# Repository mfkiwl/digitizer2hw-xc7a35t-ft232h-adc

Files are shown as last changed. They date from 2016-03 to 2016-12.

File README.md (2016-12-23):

# Digitizer2 TDC hardware
The digitizer2 project is a low-cost, high speed analog-to-digital converter with customizable signal processing logic.

Hardware
---
- Xilinx Artix7 FPGA (XC7A35T)
- 500 MHz, 12bit ADC (ADS5403)
- DDR3 Memory, 128 MB (MT41J128M16)
- USB 2.0, Hi-Speed (FT2232H)

Related repositories
---
- [FPGA device server](https://github.com/pwuertz/fpga-device-server)
- [Digitizer2 Firmware](https://github.com/pwuertz/digitizer2fw)
- [Digitizer2 Hardware](https://github.com/pwuertz/digitizer2hw)

License
---
This project is free software. You can redistribute it and/or modify it under the terms of the [GNU General Public License](COPYING.txt).

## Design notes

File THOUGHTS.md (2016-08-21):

PCB Buildup
===========

6 Layer Option
--------------

Eurocircuits 6 layer, 35µm copper inner/outer:
- layer 1
- prepreg, 0.2mm
- layer 2
- core, 0.36mm
- layer 3
- prepreg, 0.3mm
- layer 4
- core, 0.36mm
- layer 5
- prepreg, 0.2mm
- layer 6

LVDS 100 Ohm, 2x signals outer:
- reference layers 2, 3, 5
- signal layers 1, 6 (outer): W = 0.19mm, S = 0.15mm, D >= 0.3mm
- signal layer 4 (inner): W = 0.15mm, S = 0.165mm, D >= 0.34mm

LVDS 100 Ohm, 2x signals inner:
- reference layers 1, 3, 4, 6
- signal layers 2, 5 (inner): W = 0.13mm, S = 0.19mm, D >= 0.4mm

USB 90 Ohm:
- signal layers 2, 5 (inner): W = 0.163mm, S = 0.19mm

FPGA Solution
=============

FPGA:
XC7A35T-2FTG256I
Artix7, 35T, FTG256, Speed Grade 2
http://www.digikey.de/product-detail/en/xilinx-inc/XC7A35T-2FTG256I/122-1912-ND/5039076

Memory:
MT41J128M16JT-125
IC DDR3 SDRAM 2GBIT 96FBGA
RZQ/4: 60 Ohm (easier for routing?)
RZQ/6: 40 Ohm

ADC Solution
============

500 Msps, 12 bit, 1 Channel

AD9434BCPZ-500
- Analog Devices, QFP Package
- 155€, DigiKey

ADS5403
- Texas Instruments, BGA Package
- 142€, DigiKey
- Pin compatible with 2 channel version
- LVDS capable clock input

FPGA Banks
==========

The I/O in 7 series FPGAs are classed as high range (HR) or high performance (HP). The HR I/Os offer the widest range of voltage support, from 1.2V to 3.3V. The HP I/Os are optimized for highest performance operation, from 1.2V to 1.8V.
- Artix only provides HR banks

The configuration banks voltage select pin (CFGBVS) must be set to a High (VCCO_0) or Low (GND) to set the configuration and JTAG I/O in banks 0, 14, and 15 for 3.3V/2.5V or 1.8V/1.5V operation, respectively.
- use 3.3V for bank 0 (JTAG-FTDI), set CFGBVS to VCCO_0
- use JTAG only configuration mode so bank 14 and 15 are not restricted to 3.3V (http://www.xilinx.com/support/answers/57045.html)

Configuration
=============

JTAG only configuration mode: M[2:0] <= "101"

Capacitor Selection
===================

Check DC Bias: http://ds.murata.co.jp/software/simsurfing

10nF, 0402, GRM155R71C103KA01
0.1uF, 0402, GRM155R71A104KA01
0.47uF, 0402, GRM155R60J474KE19 (up to 2.5V)
1uF, 0402, GRM155R61A105KE15D (up to 2.5V)
4.7uF, 0805, GRM21BR71A475KA73 (up to 3.3V)
47uF, 1210, GRM32ER70J476ME20L (up to 2.5V)
10uF, 1206, GRM32DR61C106KA01 (up to 5.0V)

Power Supply
============

FPGA Core
- 1.0V (http://www.digikey.de/product-detail/de/analog-devices-inc/ADP2108AUJZ-1.0-R7/ADP2108AUJZ-1.0-R7CT-ND/2355507)
FPGA LVDS Banks
- 2.5V LM3671MF-2.5

ADC Supply
- 2.5V TPS79625DCQ
2mA
- 1.8V TPS79618DCQ
65mA + 35mA + 170mA + 90mA = 360mA
- 3.3V TPS79633DCQ
170mA

Modular Design
==============
Board-To-Board Differential Connectors
http://www.digikey.de/product-detail/de/samtec-inc/QTH-040-01-L-D-DP-A/SAM8849-ND/2345118
http://www.digikey.de/product-detail/de/samtec-inc/QSH-040-01-L-D-DP-A/SAM8843-ND/2345116

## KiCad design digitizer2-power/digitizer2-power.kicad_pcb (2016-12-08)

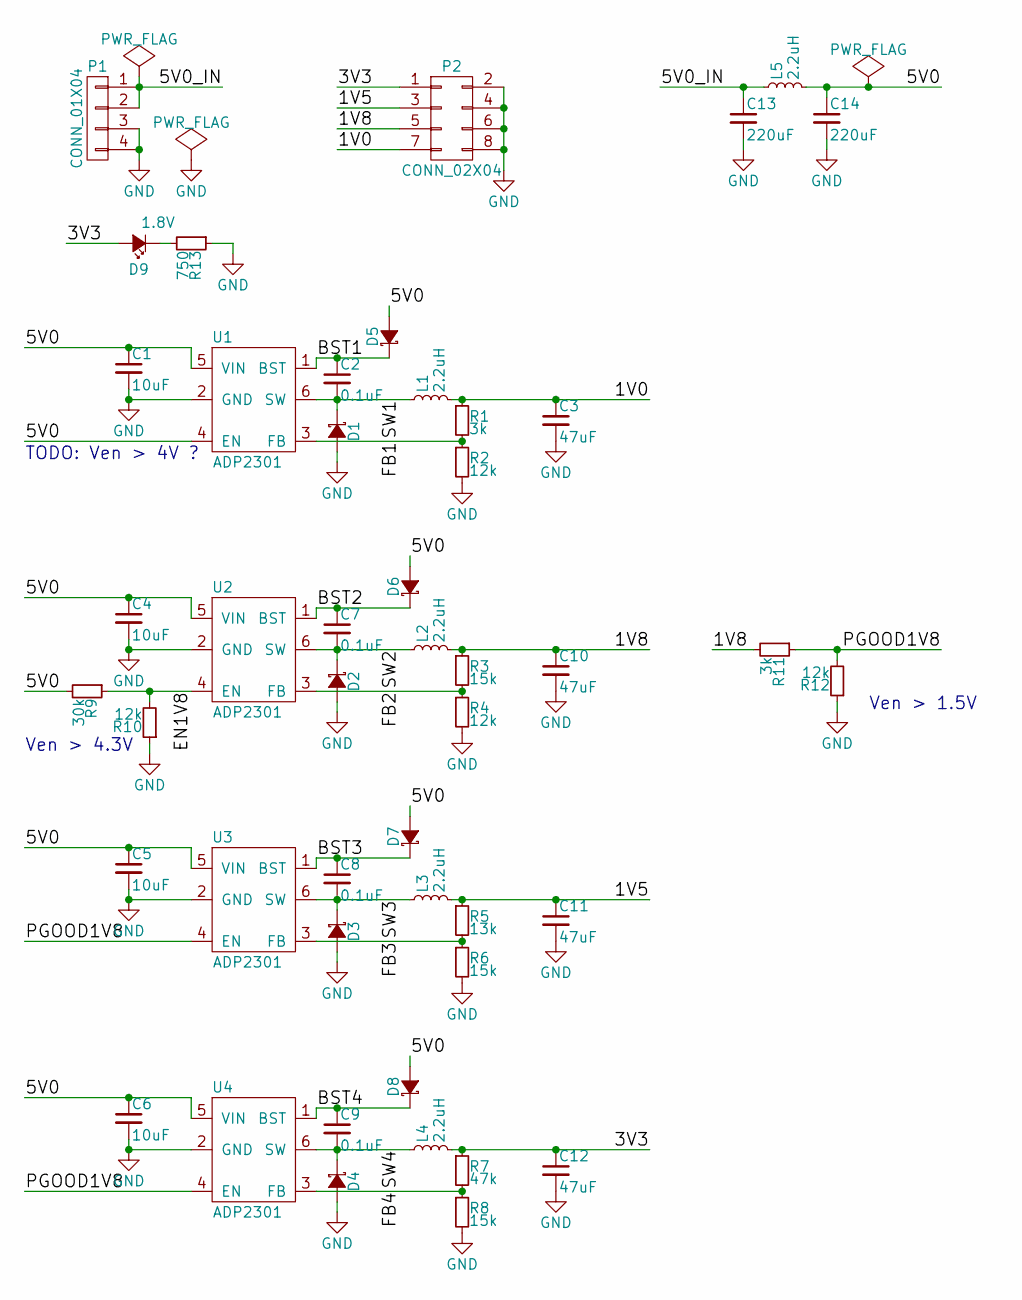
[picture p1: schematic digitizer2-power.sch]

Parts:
C1, C4, C5, C6: 10uF; C_1206; MPN GRM32DR61C106KA01L
C2, C7, C8, C9: 0.1uF; C_0603_HandSoldering; MPN GRM188R72A104KA35D
C3, C10, C11, C12: 47uF; C_1210; MPN GRM32ER61A476KE20L
C13, C14: 220uF; c_elec_5x5.7; MPN 6SVPE220MW
D1, D2, D3, D4: D_Schottky_Small; SMA_Standard; MPN B230A-13-F
D5, D6, D7, D8: D_Schottky_Small; SOD-123; MPN BAT42W
D9: 1.8V; LED_0603
L1, L2, L3, L4, L5: 2.2uH; IHLP-1212BZ-11; MPN IHLP1212BZER2R2M11
P1: CONN_01X04; Pin_Header_Straight_1x04
P2: CONN_02X04; Pin_Header_Straight_2x04
R1, R11: 3k; R_0603_HandSoldering
R2, R4, R10, R12: 12k; R_0603_HandSoldering
R3, R6, R8: 15k; R_0603_HandSoldering
R5: 13k; R_0603_HandSoldering
R7: 47k; R_0603_HandSoldering
R9: 30k; R_0603_HandSoldering
R13: 750; R_0603_HandSoldering
U1, U2, U3, U4: ADP2301; SOT-23-6; MPN ADP2301AUJZ-R7

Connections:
/1V0: C3.1, L1.2, P2.7, R1.1
/1V5: C11.1, L3.2, P2.3, R5.1
/1V8: C10.1, L2.2, P2.5, R3.1, R11.2
/3V3: C12.1, D9.2 (A), L4.2, P2.1, R7.1
/5V0: C1.1, C4.1, C5.1, C6.1, C14.1, D5.2 (A), D6.2 (A), D7.2 (A), D8.2 (A), L5.2, R9.2, U1.4 (EN), U1.5 (VIN), U2.5 (VIN), U3.5 (VIN), U4.5 (VIN)
/5V0_IN: C13.1, L5.1, P1.1, P1.2
/BST1: C2.1, D5.1 (K), U1.1 (BST)
/BST2: C7.1, D6.1 (K), U2.1 (BST)
/BST3: C8.1, D7.1 (K), U3.1 (BST)
/BST4: C9.1, D8.1 (K), U4.1 (BST)
/EN1V8: R9.1, R10.2, U2.4 (EN)
/FB1: R1.2, R2.1, U1.3 (FB)
/FB2: R3.2, R4.1, U2.3 (FB)
/FB3: R5.2, R6.1, U3.3 (FB)
/FB4: R7.2, R8.1, U4.3 (FB)
/PGOOD1V8: R11.1, R12.2, U3.4 (EN), U4.4 (EN)
/SW1: C2.2, D1.1 (K), L1.1, U1.6 (SW)
/SW2: C7.2, D2.1 (K), L2.1, U2.6 (SW)
/SW3: C8.2, D3.1 (K), L3.1, U3.6 (SW)
/SW4: C9.2, D4.1 (K), L4.1, U4.6 (SW)
GND: C1.2, C3.2, C4.2, C5.2, C6.2, C10.2, C11.2, C12.2, C13.2, C14.2, D1.2 (A), D2.2 (A), D3.2 (A), D4.2 (A), P1.3, P1.4, P2.2, P2.4, P2.6, P2.8, R2.2, R4.2, R6.2, R8.2, R10.1, R12.1, R13.1, U1.2 (GND), U2.2 (GND), U3.2 (GND), U4.2 (GND)
unnamed: D9.1 (K), R13.2

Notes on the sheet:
TODO: Ven > 4V ?
Ven > 4.3V
Ven > 1.5V

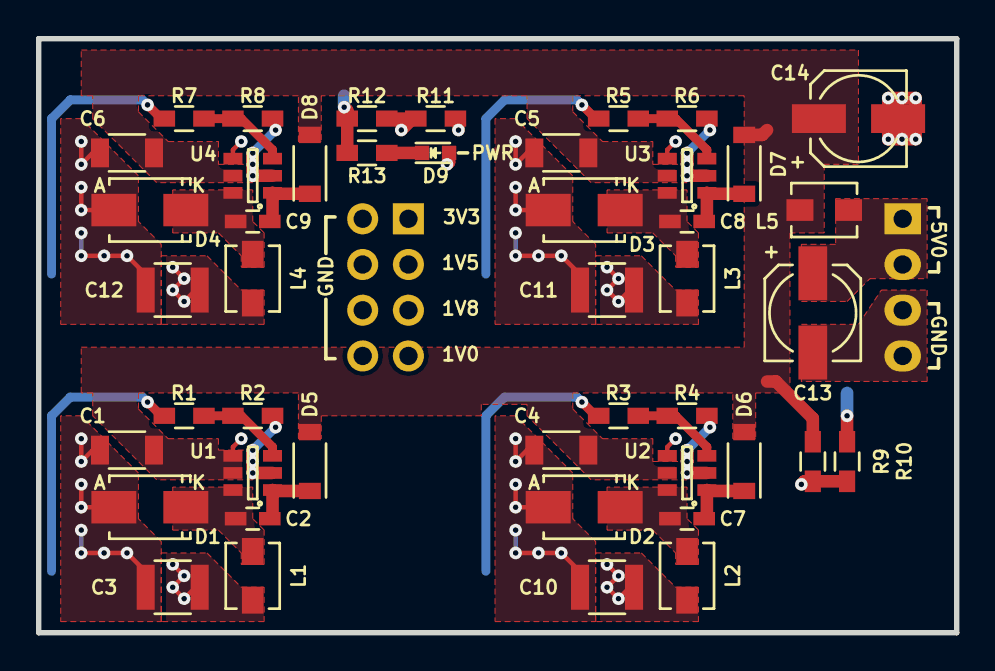
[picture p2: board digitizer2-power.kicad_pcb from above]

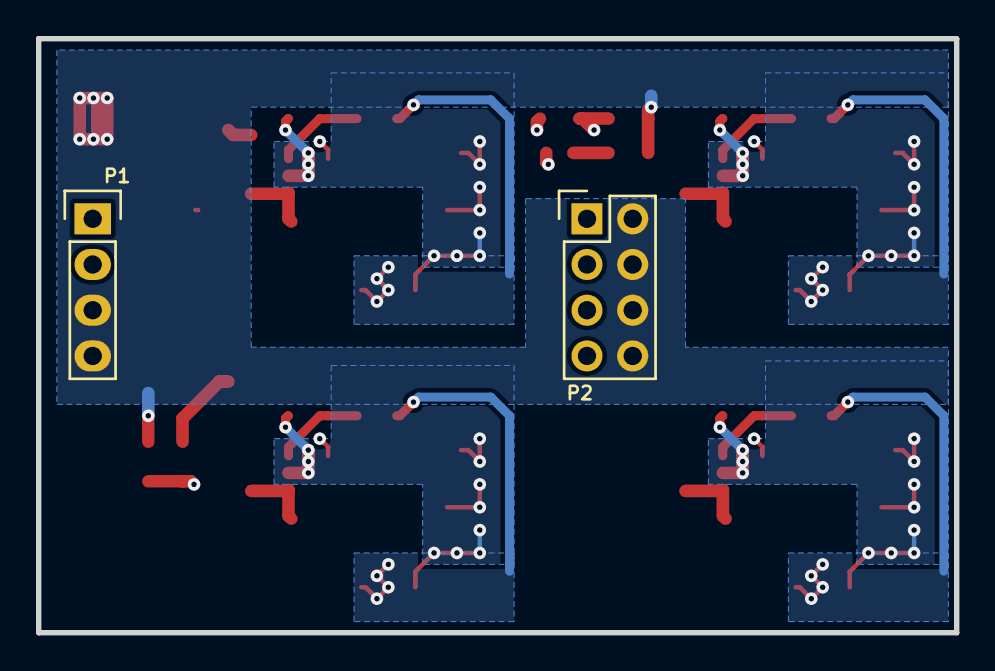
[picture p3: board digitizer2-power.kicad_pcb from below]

Board: 4 copper layers, 51.0 x 33.0 mm, 47 parts (2 on the bottom side), 22 nets.

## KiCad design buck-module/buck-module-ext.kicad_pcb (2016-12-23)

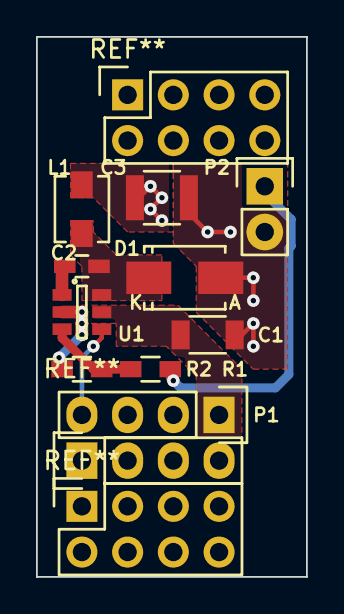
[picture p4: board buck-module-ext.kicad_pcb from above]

Board: 2 copper layers, 15.0 x 30.0 mm, 10 parts (0 on the bottom side), 7 nets.

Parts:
C1: 10uF; C_1206
C2: 0.1uF; C_0603_HandSoldering
C3: C_Small; C_1210
D1: D_Schottky_Small; SMA_Standard
L1: 2.2uH; IHLP-1212BZ-11
P1: CONN_01X04; Pin_Header_Straight_1x04
P2: CONN_01X02; Pin_Header_Straight_1x02
R1: div1; R_0603_HandSoldering
R2: div2; R_0603_HandSoldering
U1: ADP2301; SOT-23-6

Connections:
/BST: C2.1, U1.1
/EN: P1.4, U1.4
/FB: R1.2, R2.1, U1.3
/SW: C2.2, D1.1, L1.1, U1.6
/VIN: C1.1, P1.1, U1.5
/VOUT: C3.1, L1.2, P2.1, R1.1
GND: C1.2, C3.2, D1.2, P1.2, P1.3, P2.2, R2.2, U1.2

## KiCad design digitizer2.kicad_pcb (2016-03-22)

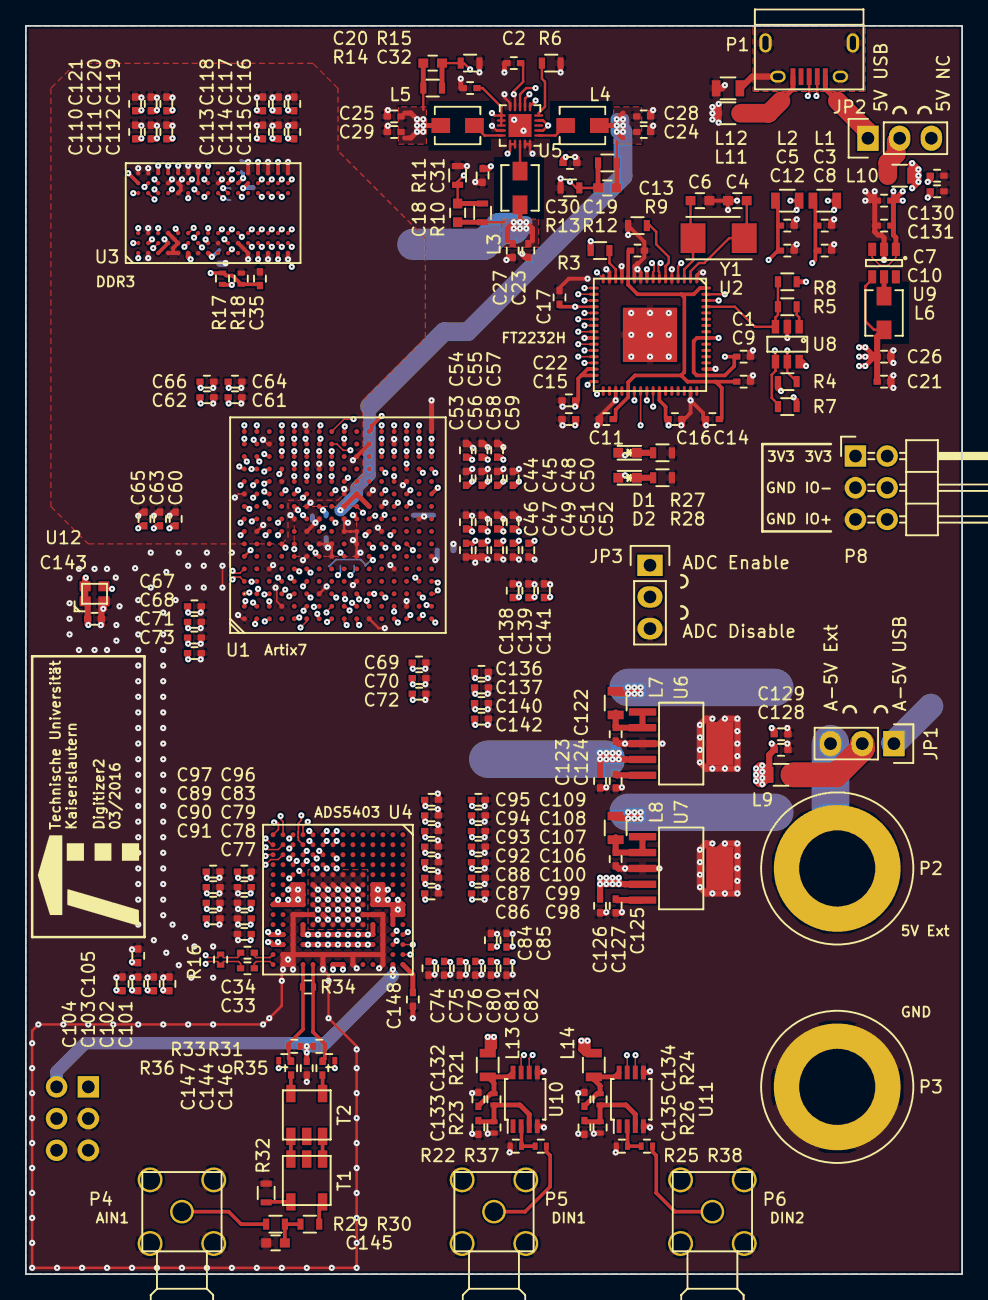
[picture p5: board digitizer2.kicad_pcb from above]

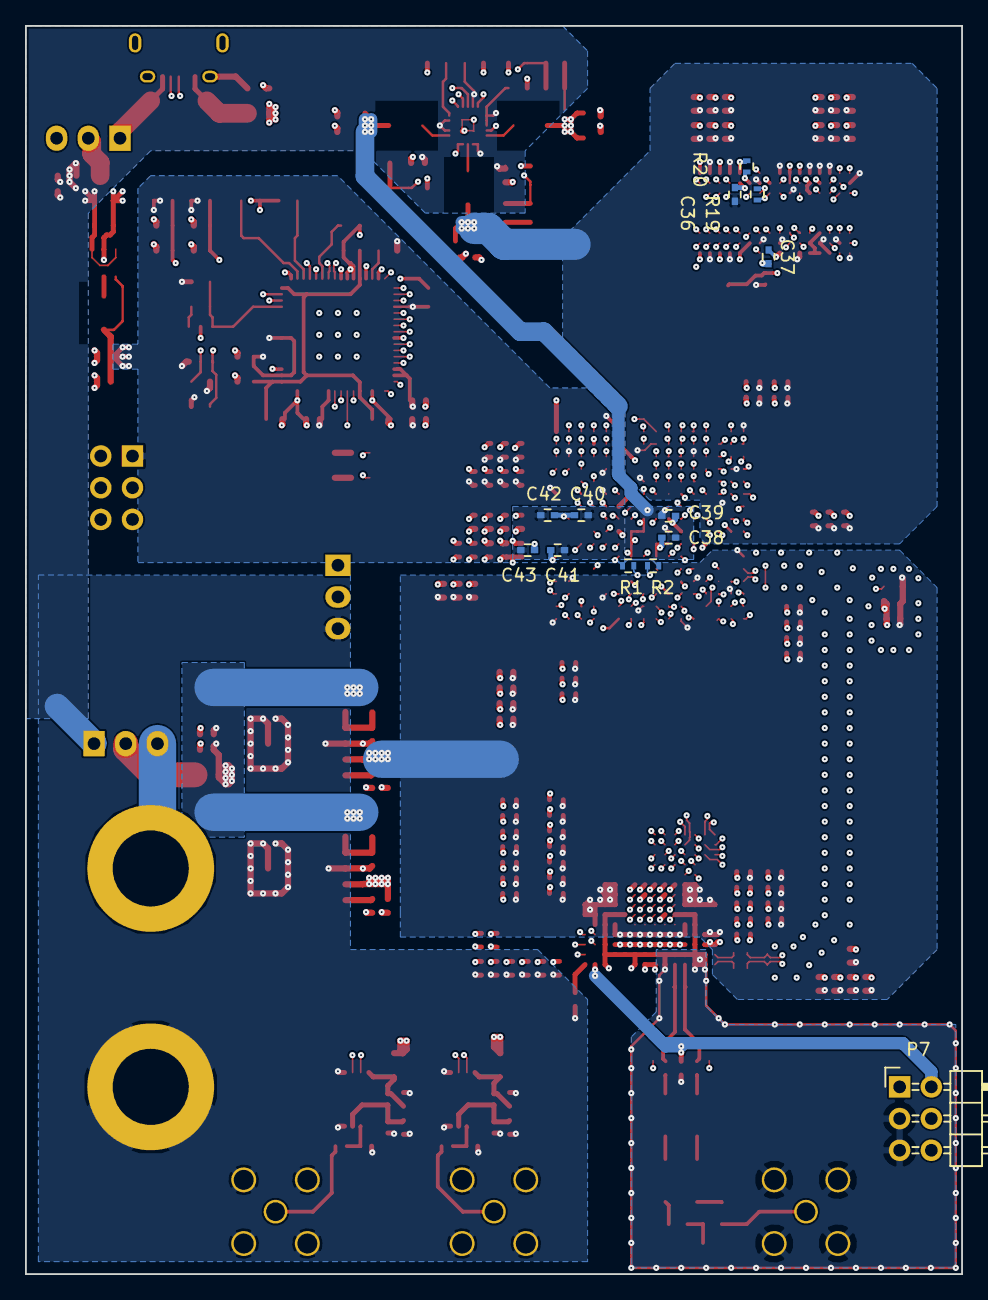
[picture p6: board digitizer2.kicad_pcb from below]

Board: 6 copper layers, 75.0 x 100.0 mm, 228 parts (13 on the bottom side), 177 nets.

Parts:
C1, C8, C11, C12, C13, C14, C15, C16, C17, C22, C33, C34, C80, C81, C82, C83, C84, C85, C92, C93, C94, C95, C96, C97, C104, C105, C106, C107, C108, C109, C116, C117, C118, C119, C120, C121, C132, C134, C143, C146, C148: 100nF; C_0402
C2, C3, C5, C7, C9, C10, C21, C23, C24, C25, C26, C27, C28, C29, C30, C31, C32, C41, C42, C47, C48, C57, C58, C64, C65, C71, C72, C122, C123, C125, C126, C128, C130, C140, C141: 4.7uF; C_0402
C4, C6: 18pF; C_0603
C18, C19, C20: 20pF; C_0603
C35, C144, C147: 1uF; C_0402
C36, C37, C74, C75, C76, C77, C78, C79, C86, C87, C88, C89, C90, C91, C98, C99, C100, C101, C102, C103, C110, C111, C112, C113, C114, C115, C124, C127, C133, C135: 10nF; C_0402
C38, C39, C40, C44, C45, C46, C51, C53, C54, C55, C56, C60, C61, C62, C63, C67, C68, C69, C70, C136, C137, C138, C139: 470nF; C_0402
C43, C49, C50, C52, C59, C66, C73, C129, C131, C142: 47uF; C_0402
C145: 6.8pF NC; C_0603
D1, D2: 1.8V; LED_0603
JP1, JP2, JP3: JUMPER3; Pin_Header_Straight_1x03
L1, L2, L7, L8, L9, L10, L11, L12, L13, L14: ferrite; R_0805
L3, L5, L6: 2.2uH; IHLP-1212BZ-11
L4: 3.3uH; IHLP-1212BZ-11
P1: USB_OTG; USB_Micro-B
P2, P3: CONN_01X01; Banana_Jack_1Pin
P4, P5, P6: SMA; SMA_ANGLE_THT
P7, P8: CONN_02X03; Pin_Header_Angled_2x03
R1, R2, R21, R23, R24, R26: 4.7k; R_0402
R3, R4, R7, R8: 10k; R_0603
R5: 2.2k; R_0603
R6, R11, R15: 200k; R_0603
R9: 12k; R_0603
R10: 175k; R_0603
R12: 125k; R_0603
R13: 100k; R_0603
R14: 50k; R_0603
R16, R19: 100; R_0402
R17, R18: 1k; R_0402
R20: 240; R_0402
R22, R25: 50; R_0402
R27, R28: 750; R_0603
R29, R30, R32: 0; R_0603
R31, R33: 25; R_0402
R34: 100 NC; R_0402
R35, R36: NC; R_0402
R37, R38: 0; R_0402
T1, T2: ETC1-1-13
U1: XC7A35T; BGA-256_pitch1mm_dia0.4mm
U2: FT2232H; QFN-FT2232HQ-64_pitch0.5
U3: MT41J128M16; BGA-96_pitch0.8mm_dia0.35mm
U4: ADS5403; BGA-196_pitch0.8mm_dia0.4mm
U5: LTC3569; UQFN-20-1EP_3x3mm_Pitch0.4mm
U6: TPS79618DCQ; SOT-223-6
U7: TPS79633DCQ; SOT-223-6
U8: 93LC46BT-I/OT; SOT-23-6
U9: LM3671MF-3.3; SOT-23-6
U10, U11: SN65LVDS100DGK; TSSOP-8_3x3mm_Pitch0.65mm
U12: ASTMLPA-18-100.000MHZ-EJ-E-T; ASTMLPA
Y1: 12MHz; Crystal_SMD_5032_2Pads

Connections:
/5V0: C2.1, C7.1, C10.1, C30.1, C31.1, C32.1, C130.1, C131.1, JP1.1, L10.1, U5.2, U5.4, U5.9, U5.11, U5.12, U5.13, U5.16, U5.17, U9.1, U9.3
/A5V0: C128.1, C129.1, L7.2, L8.2, L9.1
/ADC_CLKIN_N: C34.1, U4.P13
/ADC_CLKIN_P: C33.1, U4.P14
/ADC_DA0_N: U1.K2, U4.H3
/ADC_DA0_P: U1.K3, U4.H4
/ADC_DA1_N: U1.H1, U4.J1
/ADC_DA1_P: U1.H2, U4.J2
/ADC_DA2_N: U1.J1, U4.J3
/ADC_DA2_P: U1.K1, U4.J4
/ADC_DA3_N: U1.H3, U4.K1
/ADC_DA3_P: U1.J3, U4.K2
/ADC_DA4_N: U1.L2, U4.K3
/ADC_DA4_P: U1.L3, U4.K4
/ADC_DA5_N: U1.G1, U4.L1
/ADC_DA5_P: U1.G2, U4.L2
/ADC_DA6_N: U1.F3, U4.L3
/ADC_DA6_P: U1.F4, U4.L4
/ADC_DA7_N: U1.F2, U4.M1
/ADC_DA7_P: U1.E1, U4.M2
/ADC_DA8_N: U1.C1, U4.M3
/ADC_DA8_P: U1.B1, U4.M4
/ADC_DA9_N: U1.E3, U4.N1
/ADC_DA9_P: U1.D3, U4.P1
/ADC_DA10_N: U1.B4, U4.N2
/ADC_DA10_P: U1.A3, U4.P2
/ADC_DA11_N: U1.C3, U4.N3
/ADC_DA11_P: U1.C2, U4.P3
/ADC_DACLK_N: U1.E5, U4.H1
/ADC_DACLK_P: U1.F5, U4.H2
/ADC_ENABLE: JP3.2, U4.B11
/ADC_INA_N: C147.2, R33.1, R34.1, R36.2, U4.L14
/ADC_INA_P: C144.2, R31.2, R34.2, R35.1, U4.K14
/ADC_OVRA_N: U1.B2, U4.L5
/ADC_OVRA_P: U1.A2, U4.M5
/ADC_SAMPLE_CLK_N: C34.2, R16.1, U1.A4
/ADC_SAMPLE_CLK_P: C33.2, R16.2, U1.A5
/ADC_SCLK: U1.P1, U4.A12
/ADC_SDENB: U1.R1, U4.A13
/ADC_SDIO: U1.N1, U4.A11
/ADC_SRESET: U1.N2, U4.B12
/ADC_VCM: C146.1, P7.2, R31.1, R33.2, U4.B14
/ADC_VREF: C148.1, U4.A14
/DIN1_N: U1.R3, U10.6
/DIN1_P: U1.T2, U10.7
/DIN2_N: U1.T4, U11.6
/DIN2_P: U1.T3, U11.7
/DRAM_A0: U1.E15, U3.N3
/DRAM_A1: U1.G12, U3.P7
/DRAM_A2: U1.F15, U3.P3
/DRAM_A3: U1.D15, U3.N2
/DRAM_A4: U1.H11, U3.P8
/DRAM_A5: U1.E11, U3.P2
/DRAM_A6: U1.J16, U3.R8
/DRAM_A7: U1.E13, U3.R2
/DRAM_A8: U1.H13, U3.T8
/DRAM_A9: U1.F12, U3.R3
/DRAM_A10: U1.H14, U3.L7
/DRAM_A11: U1.H12, U3.R7
/DRAM_A12: U1.F13, U3.N7
/DRAM_A13: U1.E12, U3.T3
/DRAM_BA0: U1.D16, U3.M2
/DRAM_BA1: U1.H16, U3.N8
/DRAM_BA2: U1.G15, U3.M3
/DRAM_CAS: U1.D11, U3.K3
/DRAM_CKE: U1.J15, U3.K9
/DRAM_CK_N: R19.2, U1.F14, U3.K7
/DRAM_CK_P: R19.1, U1.G14, U3.J7
/DRAM_DQ0: U1.C13, U3.E3
/DRAM_DQ1: U1.C12, U3.F7
/DRAM_DQ2: U1.A14, U3.F2
/DRAM_DQ3: U1.C11, U3.F8
/DRAM_DQ4: U1.C14, U3.H3
/DRAM_DQ5: U1.A13, U3.H8
/DRAM_DQ6: U1.D13, U3.G2
/DRAM_DQ7: U1.B14, U3.H7
/DRAM_DQ8: U1.A9, U3.D7
/DRAM_DQ9: U1.D9, U3.C3
/DRAM_DQ10: U1.D8, U3.C8
/DRAM_DQ11: U1.A12, U3.C2
/DRAM_DQ12: U1.C8, U3.A7
/DRAM_DQ13: U1.B12, U3.A2
/DRAM_DQ14: U1.A8, U3.B8
/DRAM_DQ15: U1.B11, U3.A3
/DRAM_DQS0_N: U1.A15, U3.G3
/DRAM_DQS0_P: U1.B15, U3.F3
/DRAM_DQS1_N: U1.A10, U3.B7
/DRAM_DQS1_P: U1.B9, U3.C7
/DRAM_ODT: U1.D14, U3.K1
/DRAM_RAS: U1.G16, U3.J3
/DRAM_RESET: U1.B16, U3.T2
/DRAM_Vref: C35.1, C36.2, C37.1, R17.2, R18.1, U3.H1, U3.M8
/DRAM_WE: U1.E16, U3.L3
/DRAM_ZQ: R20.1, U3.L8
/EXT5V0: JP1.3, P2.1
/GCLK1: U1.D4, U12.3
/GPIO1_N: P8.4, U1.P11
/GPIO1_P: P8.6, U1.P10
/INA_BYPASS_N: P7.4, R36.1
/INA_BYPASS_P: P7.6, R35.2
/INIT_B: R2.2, U1.K10
/JTAG_TCK: U1.L7, U2.38
/JTAG_TDI: U1.N7, U2.39
/JTAG_TDO: U1.N8, U2.40
/JTAG_TMS: U1.M7, U2.41
/LED1: D1.2, U1.T13
/LED2: D2.2, U1.R13
/PROGRAM_B: R1.2, U1.L9
/USB_5V0: JP2.1, P1.1
/USB_CLKOUT: U1.N12, U2.32
/USB_CON_D_N: P1.2, U2.7
/USB_CON_D_P: P1.3, U2.8
/USB_D0: U1.M16, U2.16
/USB_D1: U1.M15, U2.17
/USB_D2: U1.N16, U2.18
/USB_D3: U1.N14, U2.19
/USB_D4: U1.P16, U2.21
/USB_D5: U1.P15, U2.22
/USB_D6: U1.R16, U2.23
/USB_D7: U1.R15, U2.24
/USB_GND: L11.2, P1.5
/USB_OE: U1.P13, U2.33
/USB_RD: U1.T15, U2.28
/USB_RESET: R3.1, U2.14
/USB_RXF: U1.M14, U2.26
/USB_SHD: L12.2, P1.6
/USB_TXE: U1.P14, U2.27
/USB_WR: U1.T14, U2.29
/VDD_ADC_1V8: C67.1, C68.1, C69.1, C70.1, C71.1, C72.1, C73.1, C86.1, C87.1, C88.1, C89.1, C90.1, C91.1, C92.1, C93.1, C94.1, C95.1, C96.1, C97.1, C98.1, C99.1, C100.1, C101.1, C102.1, C103.1, C104.1, C105.1, C106.1, C107.1, C108.1, C109.1, C123.1, C136.1, C137.1, C138.1, C139.1, C140.1, C141.1, C142.1, C143.1, JP3.1, U1.A6, U1.B3, U1.D7, U1.E4, U1.F1, U1.J2, U1.M3, U1.R4, U1.T1, U4.A8, U4.A9, U4.B8, U4.B9, U4.B10, U4.C6, U4.C7, U4.C8, U4.D6, U4.D7, U4.D8, U4.D10, U4.D11, U4.E11, U4.F11, U4.G11, U4.G14, U4.H11, U4.H14, U4.J11, U4.K11, U4.L6, U4.L7, U4.L8, U4.L10, U4.L11, U4.M6, U4.M7, U4.M8, U4.N8, U4.N11, U4.P8, U4.P11, U6.4, U12.1, U12.4
/VDD_ADC_3V3: C74.1, C75.1, C76.1, C77.1, C78.1, C79.1, C80.1, C81.1, C82.1, C83.1, C84.1, C85.1, C126.1, L13.2, L14.2, P7.1, U4.D12, U4.E12, U4.F12, U4.G12, U4.H12, U4.J12, U4.K12, U4.L12, U4.N12, U4.P12, U7.4
/VDD_DRAM_1V5: C18.1, C23.1, C27.1, C36.1, C60.1, C61.1, C62.1, C63.1, C64.1, C65.1, C66.1, C110.1, C111.1, C112.1, C113.1, C114.1, C115.1, C116.1, C117.1, C118.1, C119.1, C120.1, C121.1, L3.2, R10.1, R17.1, U1.A16, U1.B13, U1.C10, U1.E14, U1.H15, U1.J12, U3.A1, U3.A8, U3.B2, U3.C1, U3.C9, U3.D2, U3.D9, U3.E9, U3.F1, U3.G7, U3.H2, U3.H9, U3.K2, U3.K8, U3.N1, U3.N9, U3.R1, U3.R9
/VDD_FPGA_1V0: C20.1, C25.1, C29.1, C44.1, C45.1, C46.1, C47.1, C48.1, C49.1, C50.1, C51.1, C52.1, L5.2, R14.1, U1.E10, U1.F7, U1.F9, U1.F11, U1.G6, U1.H9, U1.J6, U1.K9, U1.L8
/VDD_FPGA_1V8: C19.1, C24.1, C28.1, C38.1, C39.1, C40.1, C41.1, C42.1, C43.1, L4.2, R12.1, U1.G8, U1.G10, U1.J10, U1.K11, U1.L10
/VDD_FPGA_3V3: C1.1, C15.1, C16.1, C17.1, C21.1, C22.1, C26.1, C53.1, C54.1, C55.1, C56.1, C57.1, C58.1, C59.1, L1.2, L2.2, L6.2, P8.1, P8.2, R1.1, R2.1, R3.2, R4.1, R7.1, R8.1, U1.E7, U1.L6, U1.L16, U1.M9, U1.M11, U1.M13, U1.N10, U1.P7, U1.R14, U1.T11, U2.20, U2.30, U2.31, U2.42, U2.50, U2.56, U8.6, U9.4
/VDD_FTDI_1V8: C9.1, C11.1, C13.1, C14.1, U2.12, U2.37, U2.49, U2.64
GND: C1.2, C2.2, C3.2, C4.2, C5.2, C6.2, C7.2, C8.2, C9.2, C10.2, C11.2, C12.2, C13.2, C14.2, C15.2, C16.2, C17.2, C21.2, C22.2, C23.2, C24.2, C25.2, C26.2, C27.2, C28.2, C29.2, C30.2, C31.2, C32.2, C35.2, C37.2, C38.2, C39.2, C40.2, C41.2, C42.2, C43.2, C44.2, C45.2, C46.2, C47.2, C48.2, C49.2, C50.2, C51.2, C52.2, C53.2, C54.2, C55.2, C56.2, C57.2, C58.2, C59.2, C60.2, C61.2, C62.2, C63.2, C64.2, C65.2, C66.2, C67.2, C68.2, C69.2, C70.2, C71.2, C72.2, C73.2, C74.2, C75.2, C76.2, C77.2, C78.2, C79.2, C80.2, C81.2, C82.2, C83.2, C84.2, C85.2, C86.2, C87.2, C88.2, C89.2, C90.2, C91.2, C92.2, C93.2, C94.2, C95.2, C96.2, C97.2, C98.2, C99.2, C100.2, C101.2, C102.2, C103.2, C104.2, C105.2, C106.2, C107.2, C108.2, C109.2, C110.2, C111.2, C112.2, C113.2, C114.2, C115.2, C116.2, C117.2, C118.2, C119.2, C120.2, C121.2, C122.2, C123.2, C124.2, C125.2, C126.2, C127.2, C128.2, C129.2, C130.2, C131.2, C132.2, C133.2, C134.2, C135.2, C136.2, C137.2, C138.2, C139.2, C140.2, C141.2, C142.2, C143.2, C145.2, C146.2, C148.2, JP3.3, L11.1, L12.1, P3.1, P4.2, P5.2, P6.2, P7.3, P7.5, P8.3, P8.5, R6.2, R9.2, R11.2, R13.2, R15.2, R18.2, R20.2, R22.2, R23.2, R25.2, R26.2, R27.1, R28.1, R32.2, U1.A1, U1.A11, U1.B8, U1.C5, U1.C15, U1.D2, U1.D12, U1.E9, U1.F6, U1.F8, U1.F10, U1.F16, U1.G3, U1.G7, U1.G9, U1.G13, U1.H6, U1.H7, U1.J8, U1.J9, U1.J11, U1.K4, U1.K6, U1.K7, U1.K8, U1.K14, U1.L1, U1.L11, U1.L15, U1.M8, U1.M10, U1.N5, U1.N15, U1.P2, U1.P12, U1.R9, U1.T6, U1.T16, U2.1, U2.5, U2.10, U2.11, U2.13, U2.15, U2.25, U2.35, U2.47, U2.51, U2.PAD, U3.A9, U3.B1, U3.B3, U3.B9, U3.D1, U3.D3, U3.D8, U3.E1, U3.E2, U3.E7, U3.E8, U3.F9, U3.G1, U3.G8, U3.G9, U3.J2, U3.J8, U3.L2, U3.M1, U3.M9, U3.P1, U3.P9, U3.T1, U3.T9, U4.C9, U4.C10, U4.C11, U4.C12, U4.C13, U4.C14, U4.D9, U4.D13, U4.E5, U4.E6, U4.E7, U4.E8, U4.E9, U4.E10, U4.E13, U4.F5, U4.F6, U4.F7, U4.F8, U4.F9, U4.F10, U4.F13, U4.F14, U4.G5, U4.G6, U4.G7, U4.G8, U4.G9, U4.G10, U4.G13, U4.H5, U4.H6, U4.H7, U4.H8, U4.H9, U4.H10, U4.H13, U4.J5, U4.J6, U4.J7, U4.J8, U4.J9, U4.J10, U4.J13, U4.J14, U4.K5, U4.K6, U4.K7, U4.K8, U4.K9, U4.K10, U4.K13, U4.L9, U4.L13, U4.M9, U4.M10, U4.M11, U4.M12, U4.M13, U4.M14, U4.N13, U4.N14, U5.10, U5.14, U5.19, U5.20, U5.21, U6.3, U6.6, U7.3, U7.6, U8.2, U9.2, U10.4, U10.5, U11.4, U11.5, U12.2
unnamed: C3.1, C8.1, L1.1, U2.9
unnamed: C4.1, U2.2, Y1.1
unnamed: C6.1, U2.3, Y1.2
unnamed: C5.1, C12.1, L2.1, U2.4
unnamed: C18.2, R10.2, R11.1, U5.7
unnamed: C19.2, R12.2, R13.1, U5.6
unnamed: C20.2, R14.2, R15.1, U5.8
unnamed: C122.1, L7.1, U6.1, U6.2
unnamed: C124.1, U6.5
unnamed: C125.1, L8.1, U7.1, U7.2
unnamed: C127.1, U7.5
unnamed: C132.1, L13.1, R21.1, U10.8
unnamed: C133.1, R21.2, R23.1, U10.3
unnamed: C134.1, L14.1, R24.1, U11.8
unnamed: C135.1, R24.2, R26.1, U11.3
unnamed: C144.1, T2.1
unnamed: C145.1, R29.1, R30.2
unnamed: C147.1, T2.2
unnamed: D1.1, R27.2
unnamed: D2.1, R28.2
unnamed: JP1.2, L9.2
unnamed: JP2.2, L10.2
unnamed: L3.1, U5.18
unnamed: L4.1, U5.1
unnamed: L5.1, U5.15
unnamed: L6.1, U9.5
unnamed: P4.1, R29.2
unnamed: P5.1, R37.2
unnamed: P6.1, R38.2
unnamed: R4.2, U2.63, U8.5
unnamed: R5.1, R8.2, U2.61, U8.3
unnamed: R5.2, U8.1
unnamed: R6.1, U5.5
unnamed: R7.2, U2.62, U8.4
unnamed: R9.1, U2.6
unnamed: R22.1, R37.1, U10.2
unnamed: R25.1, R38.1, U11.2
unnamed: R30.1, T1.2
unnamed: R32.1, T1.1
unnamed: T1.3, T2.5
unnamed: T1.5, T2.3

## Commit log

2016-03-10 Initial routing
    [digitizer2.kicad_pcb]
2016-03-11 Tuned ADC DDR layout
    [digitizer2.kicad_pcb, digitizer2.sch]
2016-03-11 Changed LVDS layout. Try new DRAM position.
    [digitizer2.kicad_pcb, digitizer2.sch]
2016-03-14 Choose final DDR3 part (MT41K and MT41J pin compatible)
    [digitizer2.kicad_pcb, digitizer2.sch]
2016-03-14 Cleanup ADC routing
    [digitizer2.kicad_pcb]
2016-03-15 DDR DQ lanes routing
    [digitizer2.kicad_pcb, digitizer2.sch]
2016-03-15 Finished DRAM DQ groups
    [digitizer2.kicad_pcb, digitizer2.sch]
2016-03-15 Begin DDR Addr/Ctrl tuning
    [digitizer2.kicad_pcb, digitizer2.sch]
2016-03-15 DRAM tuned
    [digitizer2.kicad_pcb]
2016-03-15 Realign FTDI
    [digitizer2.kicad_pcb]
2016-03-16 Layout FTDI interface
    [digitizer2.kicad_pcb, digitizer2.sch]
2016-03-16 Serial interfaces, cleanup
    [digitizer2.kicad_pcb, digitizer2.sch]
2016-03-16 Add ADC evaluation board documents, add usb tracks
    [digitizer2.kicad_pcb, digitizer2.sch]
2016-03-17 Power supply initial selection
    [digitizer2.kicad_pcb, digitizer2.sch]
2016-03-17 Config bank. Power labels
    [digitizer2.kicad_pcb, digitizer2.sch]
2016-03-17 Cleanup. Add Eeprom.
    [digitizer2.kicad_pcb, digitizer2.sch]
2016-03-18 Work on power supply
    [digitizer2.sch]
2016-03-18 Start routing power supply
    [digitizer2.kicad_pcb, digitizer2.sch]
2016-03-21 Power supply and bypass capacitors
    [digitizer2.kicad_pcb, digitizer2.sch]
2016-03-21 Prepare digital trigger and additional clock input
    [digitizer2.kicad_pcb, digitizer2.sch]
2016-03-21 Add more LVDS inputs and begin analog frontend
    [digitizer2.kicad_pcb, digitizer2.sch]
2016-03-21 Add SMA connectors
    [digitizer2.kicad_pcb, digitizer2.sch]
2016-03-22 First digitizer2 release candidate
    [digitizer2.kicad_pcb, digitizer2.sch]
2016-03-22 Add pads for input termination
    [digitizer2.kicad_pcb, digitizer2.sch]
2016-03-22 Fix DRC errors in schematic
    [digitizer2.kicad_pcb, digitizer2.sch]
2016-03-22 Edit top silk layer
    [digitizer2.kicad_pcb]
2016-03-22 Add more GND fills
    [digitizer2.kicad_pcb]
2016-03-22 Add TU KL logo
    [digitizer2.kicad_pcb]
2016-03-22 Fix GND vias
    [digitizer2.kicad_pcb]
2016-03-23 Cleanup, mark as revision 1.0
    [digitizer2.sch]
2016-03-23 Start adding order codes
    [digitizer2.sch]
2016-03-24 Replace 47uF footprints with 0805. Rev 1.1
    [digitizer2.sch]
2016-06-03 New power supply design (support pcb)
    [digitizer2-power.kicad_pcb, digitizer2-power.sch]
2016-06-29 Board revision 1.2
    [digitizer2.sch]
2016-07-22 New capacitor selection
    [digitizer2.sch]
2016-07-22 Add 3.3V -> 2.5V regulator
    [digitizer2.sch]
2016-07-26 Move power supply off-board
    [digitizer2.sch]
2016-07-28 Last tweaks for board rev 1.2
    [digitizer2.sch]
2016-08-21 Add buck module project for new power supply
    [buck-module.kicad_pcb, buck-module.sch, digitizer2-power.kicad_pcb]
2016-11-02 Build new digitizer2-power board from buck module
    [digitizer2-power.kicad_pcb, digitizer2-power.sch]
2016-12-08 Fill in last details for power supply, cleanup
    [buck-module.sch, digitizer2-power.kicad_pcb, digitizer2-power.sch]
2016-12-23 Add missing kicad files
    [buck-module-ext.kicad_pcb]
2016-12-23 Add license, update schema/pcb, add missing scripts
    [digitizer2.sch]
2017-03-07 Update USB symbol
    [digitizer2.sch]
